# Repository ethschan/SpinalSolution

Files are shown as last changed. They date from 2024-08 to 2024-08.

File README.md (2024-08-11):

# SpinalSolution: A Cerebrospinal Fluid Leakage Detection Device for the Emergency Room (2021)

<p align="center">
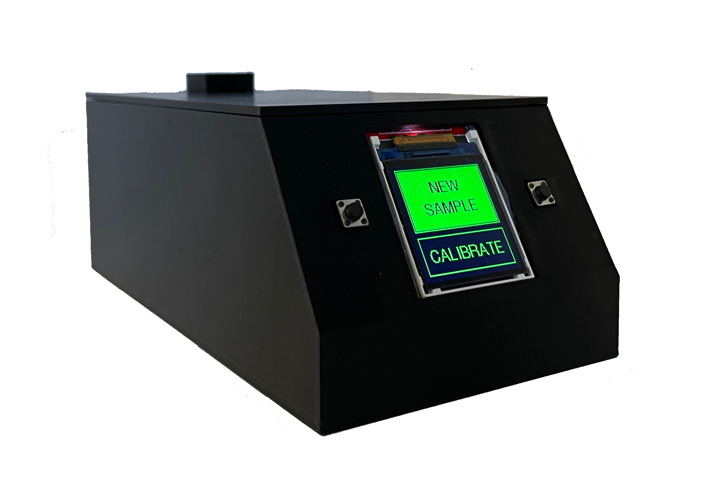
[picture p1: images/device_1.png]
Device Photo
  
  Device Internal View
</p>
<p align="center"><i>CSF leakage detection device</i></p>

## Overview

This repository contains models and code for SpinalSolution, a Grade 11 (2021) personal project aimed at developing an electronic device to detect cerebrospinal fluid (CSF) leakage in emergency rooms. The project was motivated by the need to improve the accuracy and speed of CSF detection in trauma patients, where current methods like the halo sign test often yield unreliable results.

More information about the project can be found [here](https://projectboard.world/ysc/project/spinal-solution-developing-an-electronic-device-to-detect-cerebrospinal-fluid-in-the-emergency-room).

## Our Solution

The CSF leakage detection device enhances the accuracy of CSF leakage detection by:

1. **Monitoring a Chemical Reaction**: Beta-2-transferrin found in CSF reduces gold (III) chloride to produce gold nanoparticle clusters that alter the optical properties of the sample.
2. **Leveraging Computational Power**: Through computational analysis, the device rapidly detects CSF presence by analyzing optical sensors, improving the  reliability of diagnostics.

## Hardware

- **Arduino Uno R3**: Serves as the main microcontroller for the device.
- **AS726X Spectral Sensor**: Used to measure visible light absorption and emittance.
- **1.44" TFT LCD Display**: Displays the results and status of the analysis.
- **GUVA-S12SD UV Sensor**: Used to measure ultraviolet light.
- **OpenLog SD Card Module**: For logging data to an SD card and storing configuration files.
- **Push Buttons**: Used to navigate and control the device’s functions.

## Setup

1. **3D Case and Cartridges**: Use the provided STL files to print the case that houses the components securely.
2. **Assemble Reagent Cartridges**: Utilize springs and rubber gaskets to assemble the 3D printed reagent cartridges.
3. **Wire Together the Hardware**:
    - Connect the **TFT LCD Display** to the Arduino: CS to pin 10, RST to pin 9, DC to pin 8.
    - Connect the **AS726X Spectral Sensor** to the Arduino via I2C: SDA to A4, SCL to A5.
    - Connect the **GUVA-S12SD UV Sensor** to the Arduino: Analog output to pin A2.
    - Connect the **OpenLog SD Card Module** to the Arduino: RX to pin 3, TX to pin 4, RST to pin 5.
4. **Install Libaries**:
    - Adafruit GFX
    - Adafruit ST7735
    - Sparkfun AS726X
5. **Flash the Firmware**: Use the Arduino IDE to upload the chosen Arduino sketch to the Arduino Uno R3.
6. **Build Calibration Curve and Calculation Model**: Test the device with known CSF samples to generate a calibration curve. Implement a calculation model based on your device's results.

## Files

- `/models/case_body.stl`: 3D model for the body of the device's case.
- `/models/case_lid.stl`: 3D model for the lid of the device's case.
- `/models/cartridge_container.stl`: 3D model for cartridge containers.
- `/models/cartridge_valve.stl`: 3D model for cartridge valves.
- `/models/cuvette_holder.stl`: 3D model for cuvette holders compatible with the device.
- `/src/SpinalSolution_Barebones.ino`: Arduino sketch for a barebones build.
- `/src/SpinalSolution_Detailed.ino`: Arduino sketch for a more featured build with real-time graphing.

## Circuit Schematic

<p align="center">
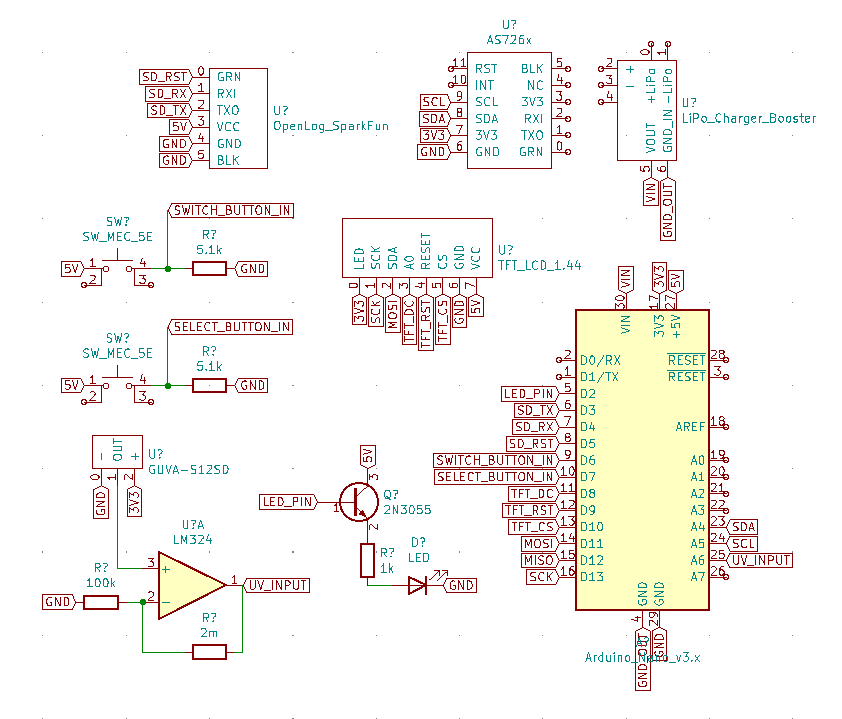
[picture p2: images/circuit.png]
Circuit schematic
  
  <i>Cicuit schematic</i>
</p>

## License

This work is licensed under the [GNU General Public License v3.0](https://www.gnu.org/licenses/gpl-3.0.en.html).

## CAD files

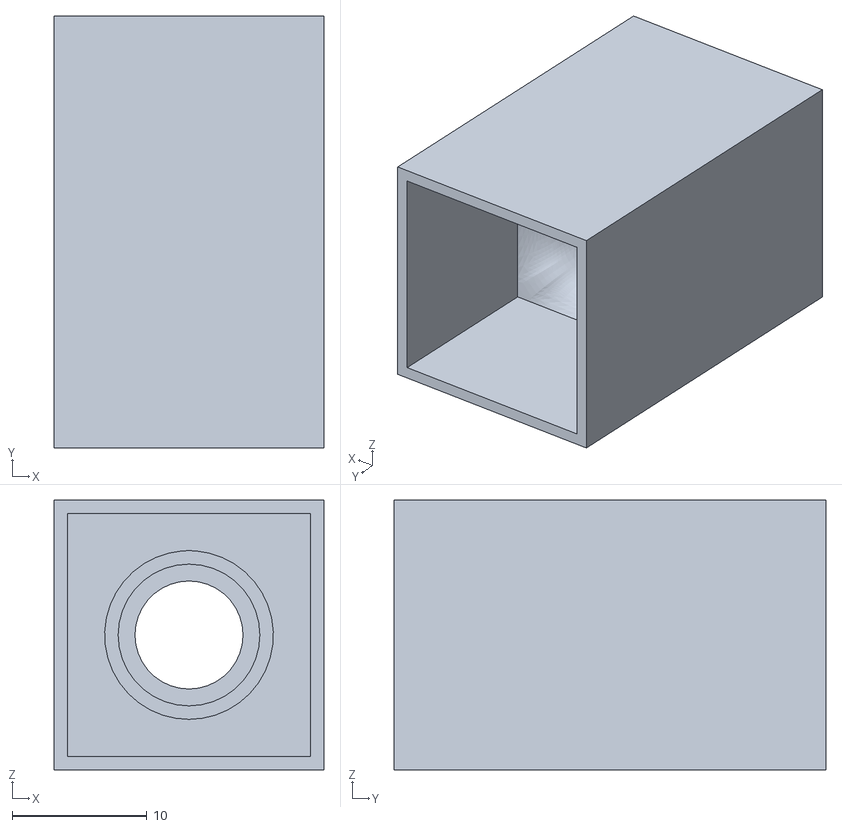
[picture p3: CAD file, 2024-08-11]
models/cartridge_container.STL
20.0 x 32.0 x 20.0

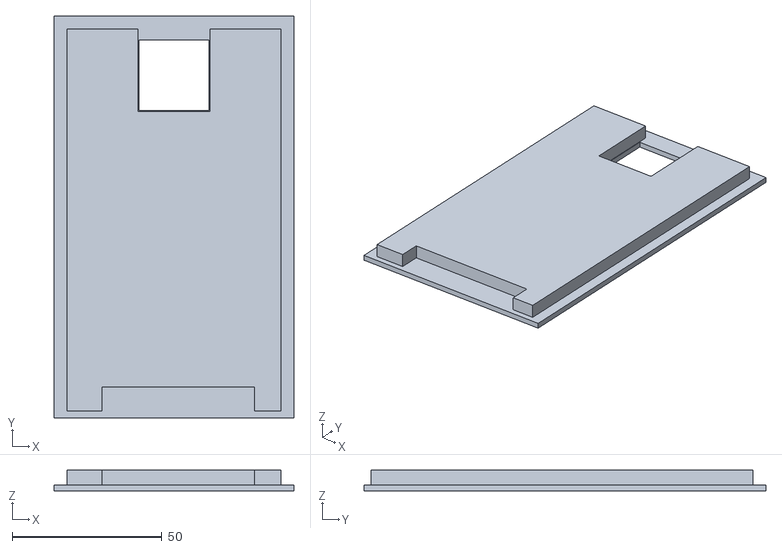
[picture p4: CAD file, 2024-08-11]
models/case_lid.STL
80.0 x 134.0 x 7.00

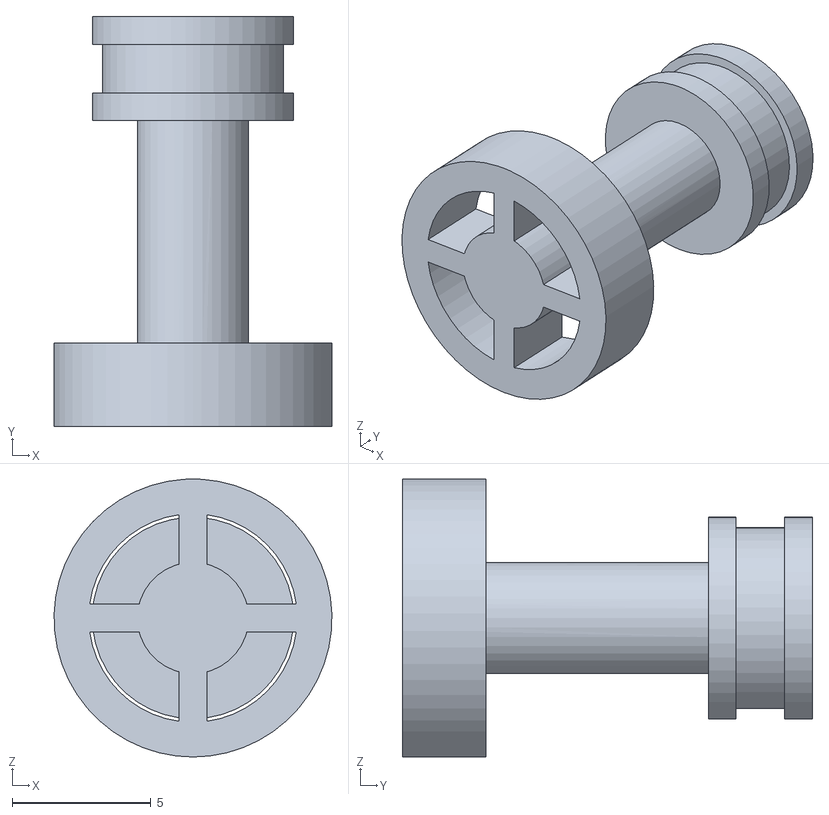
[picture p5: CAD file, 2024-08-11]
models/cartridge_valve.STL
10.00 x 14.8 x 10.0

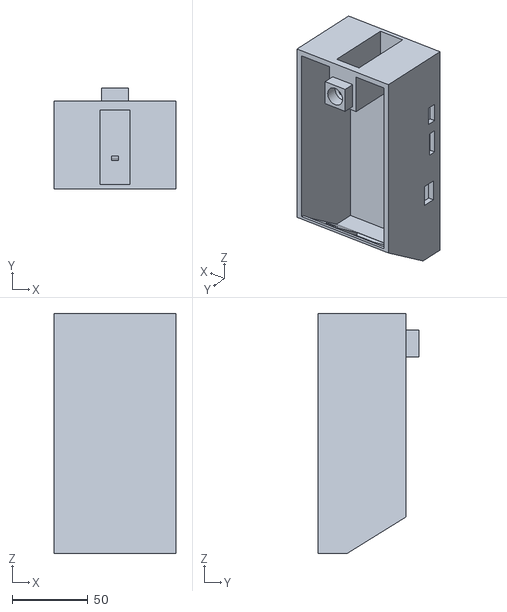
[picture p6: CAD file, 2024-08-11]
models/case_body.STL
80.0 x 66.2 x 158.0

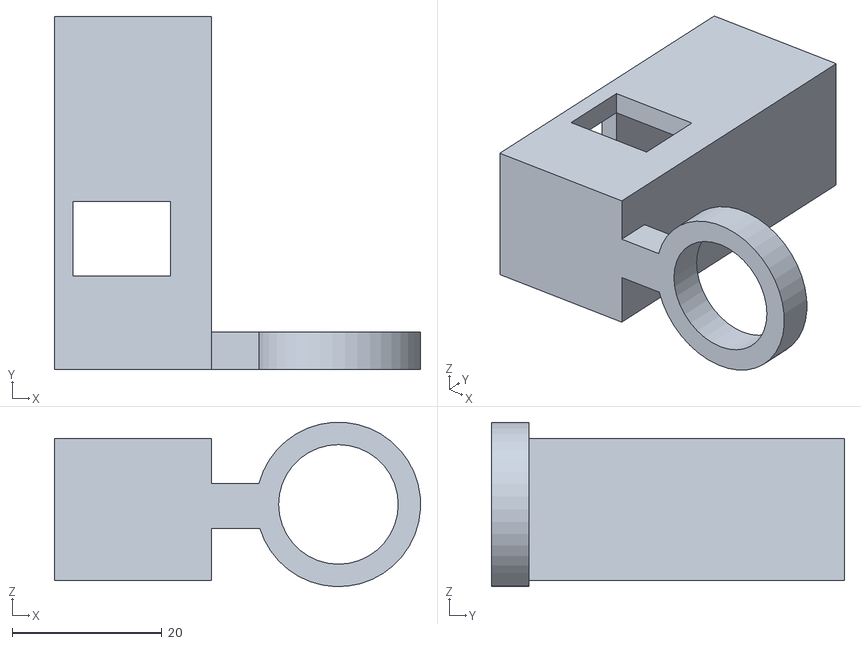
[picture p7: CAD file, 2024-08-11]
models/cuvette_holder.STL
49.0 x 47.2 x 22.0

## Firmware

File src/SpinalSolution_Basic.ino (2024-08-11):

/*
 * File Name: SpinalSolution_Basic.ino
 * 
 * Description:
 * This Arduino sketch is designed to detect cerebrospinal fluid leakage using optical sensors.
 * The device uses a series of spectral sensors to measure red, orange, yellow, green, blue, and violet light, along with a UV sensor.
 * 
 * NOTE: This sketch takes care of calibration, processing samples, and displaying results.
 * The current implementation includes placeholder calculations. You MUST build and calibrate the system yourself to obtain accurate results.
 * 
 * Hardware:
 * - 1.44" TFT LCD display connected to pins 10 (CS), 9 (RST), 8 (DC)
 * - AS726X spectral sensor connected via I2C
 * - UV sensor connected to analog pin A2
 * - Button inputs on pins 6 and 7
 * - OpenLog SD card module connected to pins 3 (RX), 4 (TX), 5 (RST)
 * 
 * Usage:
 * - Insert the sample into a cuvette and place it in the device.
 * - Push a reagent cartridge onto the spring valve.
 * - Press the button to start the measurement.
 * - Wait for results.
 * 
 * History:
 * - Original Code: March 2021
 * - Updated: August 2024 for code readability
 */

// Import Statements
#include <Adafruit_GFX.h> // Adafruit Graphics library for TFT display
#include <Adafruit_ST7735.h> // 1.44" TFT LCD library
#include <Fonts/FreeSans9pt7b.h> // Header font library
#include <Fonts/FreeMono9pt7b.h> // Text font library
#include "AS726X.h" // AS726x spectral sensor library
#include <SoftwareSerial.h> // SoftwareSerial library for serial communication with OpenLog


// Pin Definitions
#define TFT_CS 10       // TFT CS pin
#define TFT_RST 9       // TFT Reset pin
#define TFT_DC 8        // TFT DC pin
#define SD_RX 3         // SD RX Pin
#define SD_TX 4         // SD TX Pin
#define SD_RST 5        // SD RST Pin
#define selectPin 7     // Select button input pin
#define switchPin 6     // Switch button input pin
#define uvSensorPin A2  // UV sensor analog pin
#define ledPin 2        // LED pin

// Constant Definitions
#define configName "CONFIG.TXT"
#define configHeader "index,r,o,y,g,b,v,uv"

// Color Definitions
#define black ST77XX_BLACK
#define green ST77XX_GREEN
#define white ST77XX_WHITE
#define blue ST77XX_BLUE
#define red ST77XX_RED
#define orange ST77XX_ORANGE
#define yellow ST77XX_YELLOW
#define dark_green 0x1D80
#define violet 0xD81F

// State Variables
int8_t selectState = 0;
int8_t switchState = 0;
int8_t currentMenu = 0;
int8_t currentSelection = 0;

int index = 0;
float calibration[6] = {0, 0, 0, 0, 0, 0};
int uvCalibration = 0;
float timeAverages[6][10] = {0};  // Array to hold averaged values over time

// Enumeration for result types
enum TestResult { NO_LEAK, LEAK_DETECTED, RECOMMEND_FURTHER_TESTING };

// Object Definitions
Adafruit_ST7735 tft = Adafruit_ST7735(TFT_CS, TFT_DC, TFT_RST); // TFT object
AS726X spectralSensor; // Spectral sensor object
SoftwareSerial OpenLog(SD_RX, SD_TX); // SoftwareSerial for logging

// Function to display the measuring menu header
void measuringMenuHeader(void) {
  tft.fillScreen(black);
  tft.drawRect(6, 6, 116, 116, green);
}

// Function to handle the main measuring process
void measuringMenu1(void) {
  measuringMenuHeader();
  setupTextDisplay();

  float specReadings[6];
  int8_t historicSelectState = digitalRead(selectPin);
  unsigned long start_time = millis();
  unsigned long current_time;
  unsigned long past_time = 0;

  int maxlen = 50;
  double x2 = 0;
  double xy[6] = {0, 0, 0, 0, 0, 0};
  int datalen = 0;
  double initial[6];
  boolean initialTaken = false;
  int signal_resolution_multiplier = 1000000;
  int time_resolution_multiplier = 1000;
  int ms_time = 300000 / maxlen;

  startNewLog();

  while (true) {
    takeMeasurement(specReadings);
    current_time = millis() - start_time;

    double current_time_total_minutes = current_time / (60000.0 / time_resolution_multiplier);
    logData(current_time, specReadings, analogRead(uvSensorPin));

    if (!initialTaken) {
      for (int i = 0; i < 6; i++) {
        initial[i] = specReadings[i];
      }
      initialTaken = true;
    }

    if (datalen < maxlen && current_time - past_time > ms_time) {
      x2 += current_time_total_minutes * current_time_total_minutes;

      for (int i = 0; i < 6; i++) {
        xy[i] += (((signal_resolution_multiplier * specReadings[i]) / initial[i]) - 1) * current_time_total_minutes;
        updateTimeAverages(specReadings[i], i);
      }
      past_time = current_time;
      datalen++;
    }

    updateProgress(current_time_total_minutes, time_resolution_multiplier);

    if (current_time_total_minutes >= 5 || checkForButtonPress(historicSelectState)) {
      break;
    }
  }

  // Process and calculate slopes after measurement loop
  double slopes[6];
  processSlopes(xy, x2, slopes);

  // Calculate concentration and result
  double concentration = calculateConcentration(slopes, timeAverages);
  TestResult result = calculateResult(concentration);

  // Display the results
  displayResults(concentration, result);

  setHomeMenu();
}

// Function to update the time-averaged data
void updateTimeAverages(float reading, int channel) {
  static int sampleCounter = 0;
  static int averageIndex = 0;

  timeAverages[channel][averageIndex] += reading;
  sampleCounter++;

  if (sampleCounter >= 10) {  // Averaging every 10 samples
    timeAverages[channel][averageIndex] /= 10;
    averageIndex = (averageIndex + 1) % 10;  // Fixed-size array, loop back to 0
    sampleCounter = 0;
  }
}

// Function to process slopes for each channel
void processSlopes(double xy[], double x2, double slopes[]) {
  for (int i = 0; i < 6; i++) {
    slopes[i] = xy[i] / x2;
  }
}

// Function to calculate the concentration based on slopes and time-averages
double calculateConcentration(double slopes[], float timeAverages[][10]) {
  // Placeholder function for concentration calculation
  // TODO: Implement actual calibration curves and calculations here for device

  // Just returning a dummy value for now...
  return 0.0;
}

// Function to determine the test result based on concentration
TestResult calculateResult(double concentration) {
  // Placeholder function for result calculation
  // TODO: Implement actual logic to determine if there is a leak, no leak, or need for further testing

  // Just returning a dummy value for now...
  return NO_LEAK;
}

// Function to display the results on the TFT screen
void displayResults(double concentration, TestResult result) {
  tft.fillScreen(black);
  tft.setCursor(0, 0);
  tft.setTextColor(green);
  tft.setTextSize(1);
  
  tft.print("Concentration: ");
  tft.print(concentration, 2);
  tft.println(" mg/L");

  tft.setCursor(0, 20);
  tft.print("Result: ");
  switch (result) {
    case NO_LEAK:
      tft.print("No Leak");
      break;
    case LEAK_DETECTED:
      tft.print("Leak Detected");
      break;
    case RECOMMEND_FURTHER_TESTING:
      tft.print("Recommend Further Testing");
      break;
  }
}

// Function to start a new log file
void startNewLog() {
  tft.drawRect(14, 70, 100, 20, green);
  sendSDCommand("rm", "LOG.CSV", '>');
  sendSDCommand("new", "LOG.CSV", '>');
  OpenLog.print("append LOG.CSV");
  OpenLog.write(13);
  OpenLog.print(F("time,red,orange,yellow,green,blue,violet,uv"));
  OpenLog.write(26);
  OpenLog.write(26);
  OpenLog.write(26);
}

// Function to take a measurement
void takeMeasurement(float specReadings[]) {
  digitalWrite(ledPin, HIGH);
  delay(200);
  spectralSensor.takeMeasurements();
  delay(50);
  digitalWrite(ledPin, LOW);

  specReadings[0] = spectralSensor.getCalibratedRed();
  specReadings[1] = spectralSensor.getCalibratedOrange();
  specReadings[2] = spectralSensor.getCalibratedYellow();
  specReadings[3] = spectralSensor.getCalibratedGreen();
  specReadings[4] = spectralSensor.getCalibratedBlue();
  specReadings[5] = spectralSensor.getCalibratedViolet();
}

// Function to log data to OpenLog
void logData(unsigned long current_time, float specReadings[], int uvReading) {
  OpenLog.print("append LOG.CSV");
  OpenLog.write(13);

  OpenLog.print(current_time);
  for (uint8_t i = 0; i < 6; i++) {
    OpenLog.print(",");
    OpenLog.print(specReadings[i]);
  }
  OpenLog.print(",");
  OpenLog.print(uvReading);
  OpenLog.write(26);
  OpenLog.write(26);
  OpenLog.write(26);
}

// Function to update progress on TFT
void updateProgress(double current_time_total_minutes, int time_resolution_multiplier) {
  int progress = 20 * current_time_total_minutes / time_resolution_multiplier;
  tft.fillRect(14, 70, progress, 20, green);
}

// Function to check for button press
bool checkForButtonPress(int8_t historicSelectState) {
  for (int8_t i = 0; i < 80; i++) {
    delay(5);
    selectState = digitalRead(selectPin);
    if (selectState == 1 && historicSelectState == 0) {
      return true;
    }
    historicSelectState = selectState;
  }
  return false;
}

// Setup the text display settings
void setupTextDisplay() {
  tft.setTextSize(1);
  tft.setFont(&FreeMono9pt7b);
  tft.setTextColor(green);
}

// Send a command to the SD card via OpenLog
void sendSDCommand(char* command, char* filename, char confirmation) {
  OpenLog.print(command);
  OpenLog.print(" ");
  OpenLog.print(filename);
  OpenLog.write(13);
  waitForChar(confirmation);
}

// Wait for a specific character from OpenLog
void waitForChar(char c) {
  while (1) {
    if (OpenLog.available()) {
      if (OpenLog.read() == c) break;
    }
  }
}

// Set the home menu
void setHomeMenu() {
  currentMenu = 0;
  currentSelection = 0;
  homeMenu1();
}

// Home Menu Header
void homeMenuHeader(void) {
  tft.fillScreen(black);
  tft.drawRect(6, 6, 116, 70, green); // top
  tft.drawRect(6, 82, 116, 40, green); // bottom

  setHeaderText();
  tft.setTextColor(green);
  tft.setCursor(44, 34);
  tft.print(F("NEW"));

  tft.setCursor(28, 58);
  tft.print(F("SAMPLE"));

  tft.setCursor(14, 108);
  tft.print(F("CALIBRATE"));

  tft.setTextColor(black);
}

// Home Menu 1
void homeMenu1(void) {
  homeMenuHeader();
  tft.fillRect(8, 8, 112, 66, green); // top box
  tft.setCursor(44, 34);
  tft.print(F("NEW"));
  tft.setCursor(28, 58);
  tft.print(F("SAMPLE"));
}

// Home Menu 2
void homeMenu2(void) {
  homeMenuHeader();
  tft.fillRect(8, 84, 112, 36, green); // bottom box
  tft.setCursor(14, 108);
  tft.print(F("CALIBRATE"));
}

// Set header text style
void setHeaderText(void) {
  tft.setFont(&FreeSans9pt7b);
}

// Set normal text style
void setNormalText(void) {
  tft.setFont(&FreeMono9pt7b);
  tft.setTextColor(green);
}

// Button Menu Header
void buttonMenuHeader(char *button_text, uint8_t x, uint8_t y) {
  tft.fillScreen(black);
  tft.drawRect(18, 82, 92, 40, green); // bottom start
  tft.fillRect(20, 84, 88, 36, green); // bottom start

  setHeaderText();
  tft.setTextColor(black);
  tft.setCursor(x, y);
  tft.print(button_text);
  setNormalText();
}

// Confirmation Menu 1
void confirmationMenu1(void) {
  buttonMenuHeader("START", 34, 108);
  tft.setCursor(4, 26);
  tft.print(F("Confirm the"));
  tft.setCursor(13, 46);
  tft.print(F("sample is"));
  tft.setCursor(33, 66);
  tft.print(F("ready."));
}

// Confirmation Menu 2
void confirmationMenu2(void) {
  buttonMenuHeader("START", 34, 108);
  tft.setCursor(4, 26);
  tft.print(F("Prepare the"));
  tft.setCursor(17, 46);
  tft.print(F("water to"));
  tft.setCursor(9, 66);
  tft.print(F("calibrate."));
}
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
